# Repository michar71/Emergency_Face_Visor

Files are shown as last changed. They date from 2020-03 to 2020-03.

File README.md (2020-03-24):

# Emergency Face Visor
 Emergency Face Visor Design for Protection against Droplets in Face-To-Face Situations.

 This might not be the optimal solution, feel free to improve or provide feedback.
This has also not gone through stringent medical evaluation. (Obviously...)

 There is ongoing discussion that the curvature matters (protection from the side, where the air flow comes from...). If anybody has data please let me know.
 At the moment design is driven by material availability. (Shield size is US Letter...)

Right now (in the US) the main target for this design is people that have face-to-face contact (Grocery workers, restaurant-takeout etc.) to protect them or the customers.
As the situation changes it might be nessassary to push designs like these into medical use. 

## Pictures
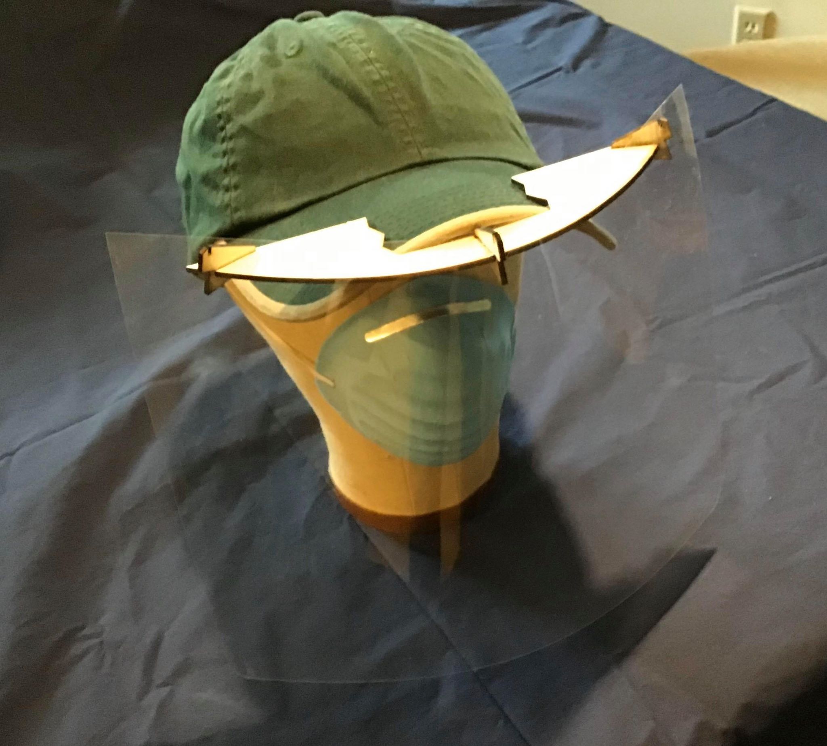
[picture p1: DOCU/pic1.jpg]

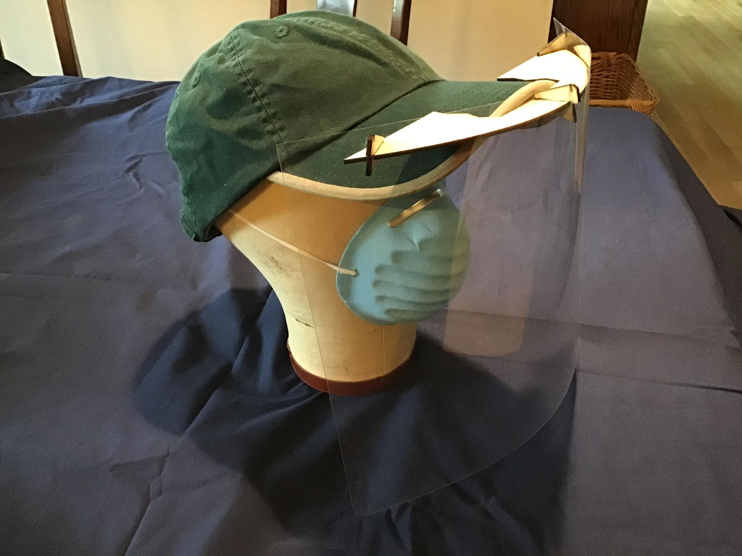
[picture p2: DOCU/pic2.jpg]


Commerically available solution
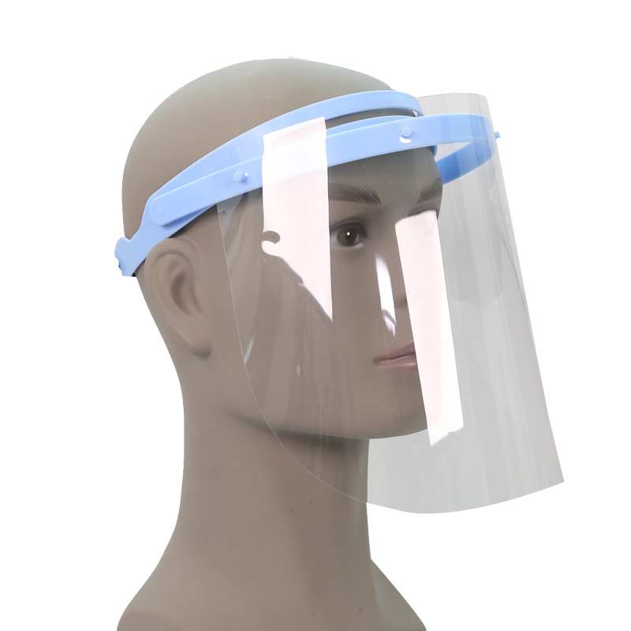
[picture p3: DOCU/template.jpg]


## Design Considerations
- Optimized Cutting Time
- Simple to assemble
- Reusable if possible
- Secure attachment to head to reduce readjusting
- Standard Materials/Tools
- Easily printable on cheap K40 lasercutters
- Includes 6x template that cuts on 9" x 11" bed
- Using mostly available 3mm (Actual 2.72mm) Plywood or acrylic
- CAD Files are designed with FreeCAD
- We tried an even simpler design with attachment points directly on the large part but the shield became too wobbly so we went back to the 4-part solution (Which uses the same amount of material)

### Standard Hole Punch Press
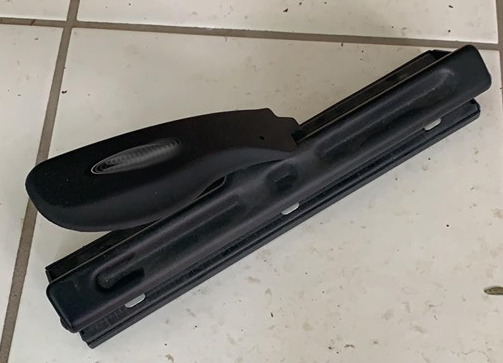
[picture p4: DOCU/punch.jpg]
Standard Punch Press


### Standard Baseball Cap
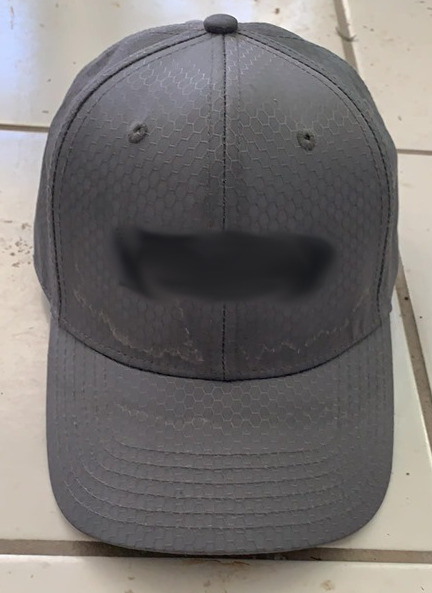
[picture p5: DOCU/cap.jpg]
Standard Baseball Cap


## Design File
Link to SVG File

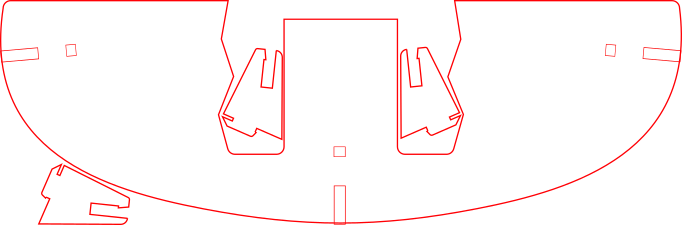
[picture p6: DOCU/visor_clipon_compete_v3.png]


## Instructions
- Download the whole repository
- Laser cut the visor_clipon_complete_v3.svg
- Attach the clips to the 3 slots (Left, Right/Middle) with the hooks in the same direction upwards.
- Punch Letter-sized transparent shield with standard American 3-Hole Punch.
- Attach shield to holder by pushing the holes over the hooks.
- Attach to cap by sliding the holder onto cap

## Notes on Laser-Cutting
- We use 3mm (Actual thickness 2.74mm) Plywood
- Cutting at 36% Power with 10mm/sec on K40
- Make sure to do a test-fit for the clip-on tabs. Depending on material thickness the slots mightr need adjustment !
- If sizes need to be adjusted due to different material thickness the attachment clips are parameterized in Freecad, the slots on the big part are easiest adjusted by creating a copy of the slot in the middle, modifying it and replacing the existing slots in Inkscape.
(Adding the slots to the CAD-Model makes it hard to still control the curvature....)

## Safety Considerations
- This is obviously not approved medical supply. But based on your circumstances it it significantly better then nothing.
- Thought was given to the fact that touching your face is bad. That's why we picked a baseball cap as the base (Besides everybody has one...) because any construction that wraps around your head is prone to slipping and adjusting....
- There is a minimum amount of open space around the attachment holes. Can be fixed with tape if this is seen as a risk.
- The visor sould be reusable if washed/desinfected in soap-water. For the clip it depends on the material. Acryic might be desinfectable, plywood is more tricky and should probably be disposed in the correct way after use.

## Alternatives
### 3D Printable Solutions

Prusa Printable Shield
[Prusa Printable Shield](https://www.prusaprinters.org/prints/25857-prusa-protective-face-shield-rc2?fbclid=IwAR09kaNTC28TPet6-zJQwPoMIv1Yob-L-BAHOmYe-wrqgnOn5zIsohTxGzE)

## Feedback
e-mail:Michael-Hartmann@gmx.net

## Version History
- V1.0 Inital Design
- V2.0 Better Wrap-Around, Small hooks to retain shield, accomodate thicker material, Optimized Shape

## Licence
Released under Creative Commons Licence, no attribution nessassary.
[Creative Commons 4.0 Licence](http://creativecommons.org/licenses/by/4.0/)

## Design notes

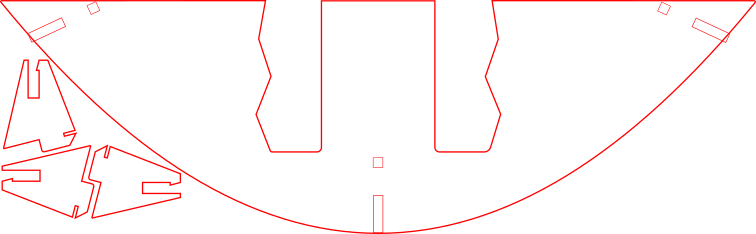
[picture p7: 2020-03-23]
DOCU/visor_clipon_compete_v2.png

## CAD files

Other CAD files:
DESIGN/visor_attachment_cap_v3.FCStd

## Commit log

2020-03-23 Inital Commit
    [visor_attachment_cap_v2.FCStd]
2020-03-23 V 2.0 Update
    [visor_attachment_cap_v2.FCStd, visor_attachment_cap_v3.FCStd]
2020-03-24 Optimize Curvature
    Optimize Curvature by making clip-on narrower and providing different angle on left/right attachment vs middle....
    [visor_attachment_cap_v3.FCStd]
